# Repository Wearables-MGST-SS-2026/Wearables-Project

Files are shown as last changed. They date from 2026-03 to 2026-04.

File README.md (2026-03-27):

# Wearables-Project

## Systemarchitektur

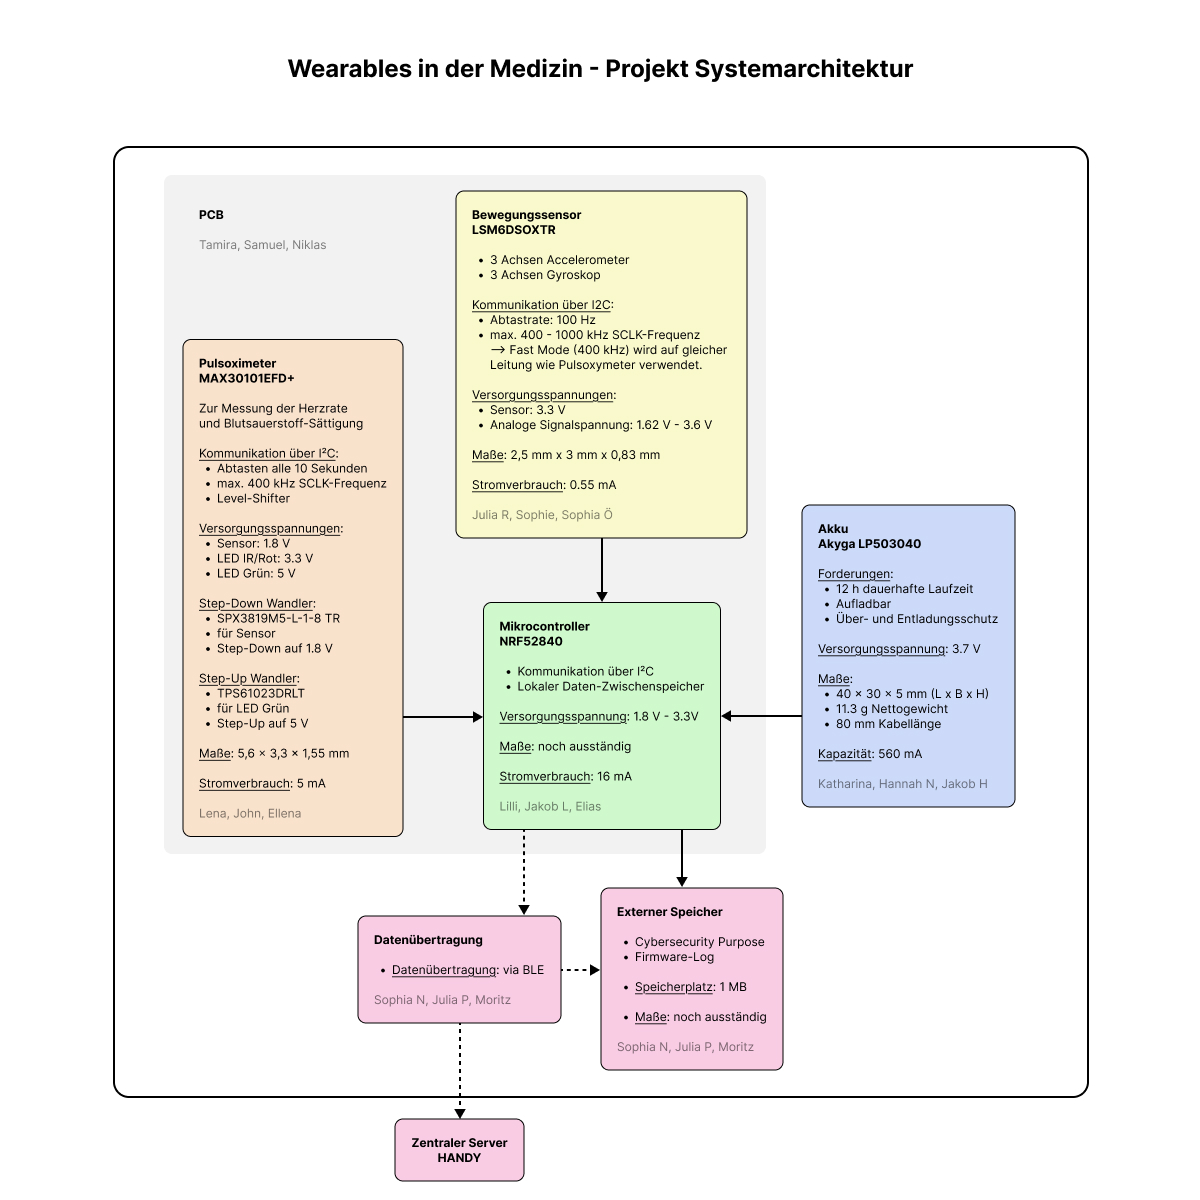
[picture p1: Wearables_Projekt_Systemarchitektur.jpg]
Systemarchitektur


Links für die Bauteile:
- Mikrokontroller: https://www.digikey.at/de/products/detail/nordic-semiconductor-asa/NRF52840-QIAA-F-R/15929794
- Akku: https://www.conrad.at/de/p/akyga-lp503040-akkupack-x-spezial-akku-lipo-3-7-v-560-mah-3385838.html
- Externer Speicher: noch ausständig
- IMU: https://www.digikey.de/de/products/detail/stmicroelectronics/LSM6DSOXTR/9841882
- Pulsoximeter:
  - Sensor: https://www.mouser.at/ProductDetail/Analog-Devices-Maxim-Integrated/MAX30101EFD%2BT?qs=sITqEBh490kEm6CNcTH1tQ%3D%3D&srsltid=AfmBOooeisLKsf-SlCmX0eI9FAGqsr9U439F-9ioyHP3WWO6gMZ4mlS4&utm_source=chatgpt.com
  - Step-Down Wandler: https://www.mouser.at/ProductDetail/MaxLinear/SPX3819M5-L-1-8-TR?qs=S%2FCBhQS5rCpfutlZ3lVq4g%3D%3D
  - Step-Up Wandler: https://www.mouser.at/ProductDetail/Texas-Instruments/TPS61023DRLT?qs=BJlw7L4Cy78Zr3IJIU3gNw%3D%3D
  - Level-Shifter für I2C: https://www.mouser.at/ProductDetail/Texas-Instruments/PCA9306DCTR?qs=wgAEGBTxy7mysSrdibj0NQ%3D%3D

### Bauteilanforderungen an Akku 
Strom_Spannungsanforderungen

## 🗓️ Deadlines

##### ➡️ 17.03.2026 (Intern)
Bauteilauswahl der verschiedenen Gruppen + eine Person, welche diese vorstellt

##### ➡️ 31.03.2026 (Extern)
Funktionalität, Architektur 
Abgabe eines Dokuments von Projektleitungsgruppe (nach Absprache mit Gesamgruppe) 

##### ➡️ 12.04.2026 (Intern)
Schaltpläne Fertigstellung

##### ➡️ 27.04.2026 (Intern)
PCB Fertigstellung

##### ➡️ 30.04.2026 (Extern)
Schaltplan und Dokumentation (Verifikation Konzept, Cybersicherheit Risiken und Konzept) 
Jede Gruppe gibt zwei Dokumente ab für ihr jeweiliges funktionales Modul:
- Schaltplan in KiCad + Bill of Materials (Teile müssen in Stock sein und JEDES Bauteil muss aufgeführt werden) 
- Dokument für Messverfahren für Verifikation und Herstellung, 2 Seiten max.)

Projektleitungsgruppe gibt ein zusätzliches Dokument bzgl. Cybersicherheit Risiken und Konzept ab 

##### ➡️ 26.05.2026 (Extern)
Wearable Challenge Tag (Alle Gruppen führen die Tests gleichzeitig)

## System Anforderungen
- am Handgelenk tragbares Wearable (Wearable zu definieren!) mit: 
  - 12 Stunden ununterbrochene Funktionalität
  - wiederaufladbare Akku (Ladebuchse muss nicht mit im Gehäuse eingeplant werden, Drahtloses laden nicht notwendig)
    - Spannungsregler notwendig? 
  - Datenübertragung zum zentrale Server
    - welche Übertragung wird genutzt? sowohl intern als auch extern= 
  - Pulsmessung
  - Bewegung Messung (min. 3 Achsen Accelerometer, min. 3 Achsen Gyroskop)
  - IPX7 Schutzklasse
  - kein User interface
  - kein Display
  - 1 Jahr Kundengarantie -> muss nach 1 Jahr immer noch 12 Stunden Laufzeit haben
  - IMU soll 100Hz Abtastrate haben
  - alle Daten müssen am Ende des Tages MIT timestamps auf dem Server sein (Sekundär Batterie muss NICHT implementiert werden), es kann angenommen werden dass Server ständig verbunden ist, aber es muss sicher gestellt werden dass keine Blockierungen passieren
  - Pulsoxy/ HR soll alle 10 Sekunden Herzrate messen & neuen Wert speichern

## Glossar
Wearable Definition:
Wearables bezeichnen Geräte, die folgende Kriterien erfüllen. Sie können nicht nur nicht obsturktiv am Körper getragen werden, sie schränken also keine Körperfunktionen ein, sondern können auch jederzeit durch die benutzende Person an- und abgelegt werden. Zudem bedienen sie sich der Sensorik, digitalen Datenverabreitung und der Kommunikation.

## Abgabe Anforderungen
- Schaltplan in KiCad designen
  - gewählte Bauteile müssen in KiCad einen Footprint besitzen
  - Testpunkte mitbedenken
  - Namen / Kennzeichnungen müssen mit Schaltplänen anderer Gruppen zusammenpassen 
- Bill of Materials:
  - Bauteile müssen kaufbar sein (keine Lieferzeiten von 12 Wochen o.ä.)
  - Eindeutige ID, Wert, Größe/Gehäuse und Bestellcode angeben
  - Beispiel BOM 
   

## Gruppen einteilung
#### Akku Gruppe 
Jakob, Hannah N., Katharina
#### Bewegungssensor Gruppe 
Julia R., Sophie, Sophia Ö. 
#### Pulsoxy/HR Gruppe 
Lena, John, Ellena
#### Projektleitunsgruppe 
Sophia G., Hauke, Marie, Hannah K. 
#### PCB Gruppe (unterstützt Akku Gruppe) 
Tamira, Niklas, Samuel 
#### Mikrokontroller Gruppe 
Jakob, Elias, Lilli 
#### Datenverarbeitungsgruppe 
Sophia N., Pietschie, Moritz

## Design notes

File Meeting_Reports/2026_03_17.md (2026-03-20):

### Update Anforderungen 
- 1 Jahr Kundengarantie -> muss nach 1 Jahr immer noch 12 Stunden Laufzeit haben 
##### IMU
- soll 100Hz Abtastrate haben

##### Datenübertragung 
- alle Daten müssen am Ende des Tages MIT timestamps auf dem Server sein (Sekundär Batterie muss NICHT implementiert werden)
- es kann angenommen werden dass Server ständig verbunden ist 
- es muss sicher gestellt werden dass keine Blockierungen passieren

##### Pulsoxy/ HR
- alle 10 Sekunden Herzrate messen & neuen Wert speichern 

### Bauteilauswahl 
#### Pulsoxy/HR
MAX30101 
- I2C
  - 400khZ maximale SCL clock freqeuncy 
- VLed grün braucht 5V
- VDD-1,8V
- ViR und Vred -> 3.3V
- 5mA

#### IMU
LSM6DS
- I2C 
  -  clock frequenzy 1000kHz (fast plus mode) 
  -  400kHZ (fast mode) -> geht auf gleicher Leitung wie HR/Pulsoxy sensor 
- 0.55 mA 
- 3,3V Versorgungsspannung 
- 1.62V-3.6V analoge Signalspannung 

#### Mikrokontroller 
nRF52840 
- BLE übertragung 
- 1,8-3,3V versorgungsspannung
- 16mA 

#### Akku 
Akyga LP503040
- 560mA 
- 3.7 V
- Kabellänge: 80 mm
- Länge: 40 mm
- Breite: 30 mm
- Höhe: 5 mm
- Nettogewicht: 11.3 g

### TO DO: 
- akku systemblock diageramm dings (Leitung) 
- systemarchitektur updaten mit ausgewählten Bauteilen (Sophia) 
- update read.me mit neuen Kundenanforderungen 

### Fragen 

### Sonstiges

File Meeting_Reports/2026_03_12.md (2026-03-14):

# Meeting Report - 12. März

Interne Deadlines:
* Bauteile raussuchen bis 17.03.
* Schaltpläne bis 12.04.
* PCB bis 27.04.

## General
* Systemarchitektur: EKG fällt weg, weil Puls bereits beim Pulsoxi gemessen wird
* Teams können intern eigene Projects mit Issues erstellen, aber sollten alles Wichtige im großen Project dokumentieren
* Aitor zum Repo einladen

## Gruppe Projektleitung
* Funktionalität basiert auf einer IU (Intended Use) + Kommunikation + Spannung

## PCB Gruppe
* Switch auf KiCad

## Gruppe Akku
* Überladungs- und Entladungsschutz einbauen (weil Medizinprodukt)
* KEIN Ladeszenario, nur Konzept (Wireless Charging oder so, muss aber eben nicht ins Design implementiert werden)
* Blockdiagramm erstellen (Tool: Webench Power Designer)

## Gruppe Datenübertragung
* Zentraler Server = Handy (muss nicht noch weiter übertragen werden)

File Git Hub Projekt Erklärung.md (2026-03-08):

### Repository
#### Dokumente 
Repository dient als Aufbewahrungsort für alle wichtigen Dokumente: 
- Erklärungsdokumente
- Dokumente für Abgaben (Schaltpläne, etc.)
- andere wichtige Dokumente (z.B. PCB Design Guidelines)

Alle sollten Berechtigung haben Dokumente zu bearbeiten und neue Dokumente hinzuzufügen.

#### Issues Übersicht
Im Repository selbst können ALLE assozierten Issues/To Dos eingesehen werden, die Verwaltung dieser ist jedoch einfacher über das Projekt selbst (siehe unten). 

### Project
Das Projekt 'Wearables Projekt Übersicht' ist mit dem Repository verbunden und wird für die gesamte Organisation des Gruppenprojekt genutzt. 
Es gibt verschiedene Ansichten um das Projekt und alle Issues zu sehen: 
- Backlog
- Board
- Calendar
- My items
  
#### Organisatorisches 
##### Meeting Protokolle & Agendas 
- Protokollierung aller Meetings wird von der Projektleitungsgruppe, damit alle auf dem gleichen Stand sind
- Erstellung von To Do's als Issues 
- Erstellung von Agendas für das jeweilige nächste Meeting von der Projektleitungsgruppe im vorhinein
  - Bearbeitbar von Allen falls weiter Punkte besprochen werden müssen

- Bei zusätzlichen kleineren Meetings mit anderen Gruppen, z.B. Akkugruppe mit Mikrokontrollergruppe, erstellt bitte ein Issue mit kurzen Notizen was besprochen wurde oder welche Entscheidungen getroffen wurde, dadurch bleiben auch in Krankheitsfällen o.ä. alle auf dem gleichen Stand. 

##### Labels & Target Dates
- Versehen aller Issues mit Labels und Target Dates -> zeitliche Dringlichkeit sichtbar in Kalender view & Filterung nach Labels für jeweilige Gruppen möglich <br>
  → Wenn ihr weitere Issues erstellt, benutzt bitte Labels und Target Dates! 

##### Assignees 
Diesen Punkt besrpechen wir im Meeting am 12.März 

##### To Do / In progress / Done 
Bitte verschiebt eure Issues in die jeweiligen Kategorien, damit es übersichtlich bleibt und alle sehen können auf welchem Stand wir gerade sind. 

#### Discussions 
Die Diskussions Funktion ist wie ein Forum und kann für alles benutzt werden, was nicht bis zum nächsten Meeting warten kann o.ä., dadurch bleibt alles etwas übersichtlicher und ist leicht wieder zu finden. Bitte erstellt relevante Categorys für euer Anliegen.

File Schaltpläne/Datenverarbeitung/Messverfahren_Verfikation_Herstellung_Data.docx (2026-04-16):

Messverfahren für Verifikation und Herstellung Datenübertragen

A. Bluetooth-Verbindung (Antenne)

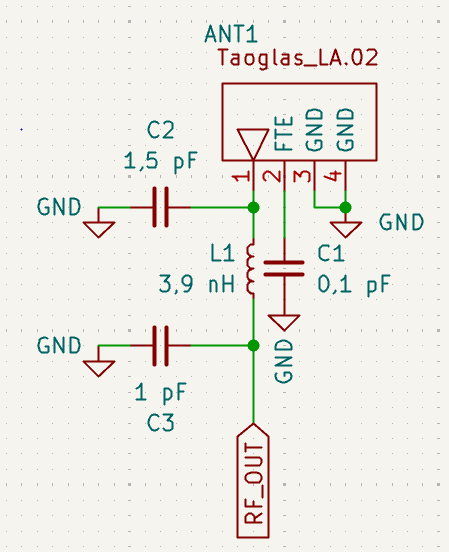
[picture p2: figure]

1. Verifikationstest (Entwicklung)

Test 1: Auffindbarkeit Testen

Überprüfen, ob das Wearable BLE-Advertising-Pakete sendet und vom Endgerät auffindbar ist.

Ablauf:

1. Wearable anschalten und in Pairing-Modus (Advertising aktivieren)
2. Scan-App/ BLE-Einstellung des Endgeräts zum Suchen nutzen
3. MAC-Adresse und Broadcast-Name prüfen
4. Wiederholen in 1m, 3m, 5m Entfernung

Erwartung:

- Wearable signalisiert Pairing-Bereitschaft
- Wearable ist auffindbar
- Name und Adresse stimmen mit Programmierung überein
- Entfernungen können toleriert werden

Test 2: Signalstabilität (RSSI/ Received Signal Strength Indicator)

Überprüfen, ob die RSSI unter Last stabil ist, um sicherzustellen, dass eine zuverlässige Verbindung gewährleistet werden kann (Antenna-Matching). Für diesen Test wird eine UART-Konsole/RSSI-Monitoring-App sowie Endgerät und Wearable benötigt.

Ablauf:

1. Wearable und Endgerät koppeln mit 1m Distanz
2. UART muss BLE_CONNECTED zeigen
3. 60s Referenzmessung
4. 60s Stresstest: Hand auf Wearable (Dämpfung durch Körper)
5. 5min Langzeittest

Erwartung:

- Referenzmessung: -40dBm bis –60dBm (bei 1m Distanz)
- Stresstest: RSSI-Abfall < 20dBm
- Langzeittest: keine Verbindungsabbrüche (BLE_DISCONNECTED)
- RSSI-Schwankung <5dBm
2. Herstellungstest

Für beide Tests wird zusätzlich zum Wearable und dem Endgerät ein UART benötigt.

Test 1: Verbindungsstatus und Fehler-Auswertung

Ablauf:

1. Wearable einschalten und über den Prüfadapter eine Verbindung zum Test-Endgerät erzwingen. Den UART-Stream auf das Event "Connected" scannen. Automatische Hardware-Diagnose beim Systemstart ausführen.
2. Ein Test-Datenpaket vom Endgerät an das Wearable senden und das Quittierungssignal (ACK) im UART-Log abfangen.
3. Die Verbindungsparameter während einer aktiven Sitzung aus dem Controller-Stack auslesen (via HCI-Kommandos).
4. Den Zeitraum zwischen Start des Advertisings und Timeout überwachen.

Level 1: Info

- Fokus: Verbindungsstatus
- Ausgabebeispiel: BLE_CONNECTED, BLE_DISCONNECTED
- Bedeutung / Ziel: Bestätigt, dass der Handshake erfolgreich war und das Wearable die Funkverbindung hält.

Level 2: Data

- Fokus: Paket-Überprüfung
- Ausgabebeispiel: Sent: [0xAF, 0x01, 0xFF], ACK received
- Bedeutung / Ziel: Prüft, ob die Datenrate für Firmware-Updates (OTA) und Sensordaten optimiert ist.

Level 3: RF/Stack

- Fokus: Protokoll-Ebene
- Ausgabebeispiel: HCI Event: Command Complete, Connection Interval: 30ms
- Bedeutung / Ziel: Verifiziert die Energieeffizienz und die korrekte Signalaushandlung der Antenne.

Level 4: Error

- Fokus: Fehlersuche
- Ausgabebeispiel: ERROR: Advertising Timeout
- Bedeutung / Ziel: Funktions-Check: Wearable hat niemanden zum Koppeln gefunden (Endgerät prüfen).

Level 4: Error

- Fokus: Fehlersuche
- Ausgabebeispiel: Crystal Oscillator unstable
- Bedeutung / Ziel: Hardware-Check: Der 32MHz Quarz ist schlecht verlötet oder defekt. Gehäuse muss getauscht werden.

Test 2: Re-Connectivity

Überprüfen, ob die Verbindung nach Trennung automatisch wieder aufgenommen wird.

Ablauf:

1. Verbindung herstellen

2. Verbindungsabbruch durch:
a) Endgerät außerhalb der Reichweite
b) Bluetooth deaktivieren
3. Geräte wieder annähern/ Bluetooth reaktivieren

Erwartung:

- Wearable startet automatisch das Advertising

B. Flash-Speicher (Cybersecurity)

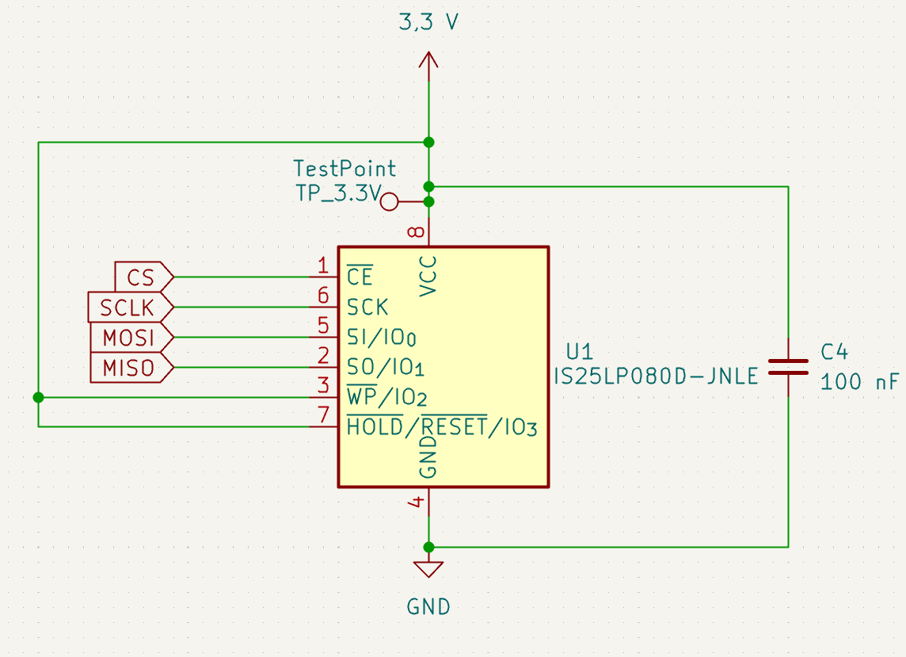
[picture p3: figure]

Testpunkt:

- TP_3.3V: Testen der Versorgungsspannung VCC
- TP_GND: Referenzmasse für Messungen

1. Verifikationstests
Test 1: Verifikation der Versorgungsspannung

Überprüfung, ob VCC = 3.3 V entspricht und unter Last stabil bleibt.

Ablauf:

1. Multimeter Sonden an TP_3.3V (rote Sonde) und TP_GND (schwarze Sonde) anlegen
2. Labornetzteil auf 3.3 V einstellen
3. DC-Spannung am Multimeter ablesen
4. Lastprüfung: Oszilloskop an TP_3.3V anschließen und AC-Kopplung zur Messung des Spannungsrippels aktivieren, während Speicher aktiv ist.

Erwartung:

- DC-Wert: 3,3 V ± 5%
- Spannungsripple unter Last: < 50mV (Peak-to-Peak)

Test 2: Verifikation der Speicherfähigkeit

Überprüfung, ob der Flash-Speicher korrekt auf Adressanfragen reagiert und gespeicherte Daten richtig zurückgibt. Der Test wird durch eine Firmware auf dem Mikrocontroller ausgeführt

Ablauf:

1. System starten und Flash-Speicher initialisieren
2. Chip Select aktivieren (auf LOW setzen)
3. Sektor löschen und bekannten Wert an definierte Adresse schreiben
4. Leseanfrage über SPI-Schnittstelle an Speicher senden
5. Adresse übertragen
6. Daten von Speicher empfangen und Chip Select deaktivieren (auf HIGH setzen)

Erwartung:

- Gelesene Daten entsprechen den zuvor geschriebenen Werten
- Bei wiederholter Abfrage derselben Adresse werden identische Datenwerte geliefert

2. Herstellungstests

Schritt | Prüfschritt | Testpunkt | Bewertungskriterium
1 | Spannungsprüfung | TP_3.3 V & TP_GND | 3.3 V ± 5%, stabil
2 | Schnittstellencheck | Über SPI | Gültige Hersteller-ID (0x9D)
3 | Write-Test | Über SPI | Schreiben ohne Fehler
4 | Read Test | Über SPI | Gelesene Daten = geschriebene Daten
5 | Endbewertung | | Bauteil als funktional oder fehlerhaft markieren

Für die Durchführung wird ein Prüfadapter mit Kontaktierung der relevanten Testpunkte sowie eine mikrocontrollerbasierte Teststeuerung (z. B. SPI-Testprogramm) benötigt.

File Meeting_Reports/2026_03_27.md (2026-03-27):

### Schaltpläne 
- Erinnerung Deadline 12.4 bis dann müssen Schaltpläne & Bill of Materials 
- Verbindungen mit Kontaktgruppen (v.a. Akku, Mikrokontroller) -> einigt euch wer welche welche Bauteile einplant die dazwischen sind 
- Testpunkte/ Kontaktpunkte für Programmierung 
- Erinnerung Messverfahren Dokument für Verifikation und Herstellung muss auch abgegeben werden (pro Gruppe) 

### 1. Abgabe - Funktionalität & Systemarchitektur 
- durchlesen bitte und KOmmentare an uns: 
https://github.com/Wearables-MGST-SS-2026/Wearables-Project/blob/main/Funktionalit%C3%A4t.md

### Sonstiges 
- bitte updated den Progress bei euren issues regelmäßig

### Fragen an Aitor 
- externer Speicher für Cybersecurity notwendig -> benutzt den kleines Flashspeicher mit 1Mb Speicher 
- Timestamps müssen im Konzept von der Mikrokontrollergruppe beachtet werden

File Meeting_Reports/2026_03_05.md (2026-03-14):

### Besprochene Punkte:
#### Entwicklung
Kunden Anforderungen inklusive Klärung noch offener Fragen, siehe aktuell definierte Anforderungen in readme.md
Systemarchitektur: gemeinsame Ausarbeitung, siehe aktuellen Stand in readme.md

#### Gruppeneinteilung
Siehe Gruppeneinteilung und Zuteilung in read me file, jede Gruppe ist für ein funktionales Modul verantwortlich mit zwei Besonderheiten:
- Die Gruppe, welche das finale PCB designt hat kein eigenes funktionales Modul, aber unterstützt die Akku Gruppe, da der Akku das aufwändigste Modul ist
- Die Projektleitungsgruppe hat ebenso kein eigenes funktionales Modul, aber es wird kontinuierlich besprochen welche andere Gruppe möglicherweise Unterstützung braucht
Entscheidung über zu benutzende Software für Schaltplan Erstellung: KiCud, wichtig hierbei ist, dass die verwendeten Bauteile in KiCad ein Design footprint haben

#### Fragenklärung
Fragenklärung bzgl. welche Aufgaben von wem ausgearbeitet & abgegeben werden müssen:
- Alle Dokumente welche als Gesamtgruppe abgegeben werden müssen ( Funktionalität & Architektur, Cybersicherheit Risiken & Konzept), werden von der Projektleitungsgruppe verfasst und abgegeben, nach gemeinsamer Besprechung und Beitragen aller
- Alle von Untergruppen abzugebende Dokumente (Schaltpläne für funktionales Modul, Messverfahren für Verifikation & Herstellung) werden von den jeweiligen Gruppen verfasst und nach Prüfung auf Kompatibilität mit anderen Gruppen abgegeben
- ALLE Untergruppen müssen nach vollständigem Design und Abgabe ein eigenes Gehäuse konstruieren und bauen für die Testung

#### Organisatorisches
Die Projektleitungsgruppe wird zeitnah eine Agenda für das nächste Meeting erstellen, mit allen zu besprechenden Punkten, bei Besprechungswünschen fügt euren Agendapunkt im vorhinein hinzu oder kontaktiert die Projektleitungsgruppe mit Wünschen & Anregungen
Nach den Meetings wird die Agenda mit dem Besprochenen ausgefüllt und als Meetingprotokoll gespeichert, sollten im Nachhinein noch Informationen fehlen, bitte als Kommentar zu fügen, damit
Alle wichtigen Informationen zum Projekt sind in der Readme File zu finden
Alle wichtigen Informationen bzgl. des Repositoriers (Erklärungen zur Nutzung etc.) sind in der git Hub Projekt Erklärung File zu finden.

#### To dos
- Recherche der einzelnen Gruppen bzgl Bauteilen/Möglichkeiten bis zum nächsten Meeting (12. März)
- Leitungsgruppe setzt Git-Repository auf, teilt es und erklärt in nächstem Meeting (12. März)
- Leitungsgruppe protokolliert dieses Meeting und setzt Agenda für nächstes auf

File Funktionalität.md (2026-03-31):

### Funktionalität
Das System ist ein am Handgelenk tragbares Wearable zur kontinuierlichen Erfassung von Vital- und Bewegungsdaten im Alltag. Es dient der Erhebung von Daten zur Herzfrequenz, Sauerstoffsättigung sowie Bewegungsinformationen des Nutzers.
Die erfassten Daten werden drahtlos an ein externes Endgerät, beispielsweise ein Smartphone, übertragen und dort gespeichert. Das Wearable selbst verfügt über keine Anzeige- oder Bedienelemente und arbeitet vollständig autonom im Hintergrund.
Das System ist für den täglichen Einsatz über eine typische Nutzungsdauer von 12 Stunden ausgelegt und für wiederholte Ladezyklen konzipiert.  Es ist für den Einsatz im Alltag geeignet und gegenüber äußeren Einflüssen wie Feuchtigkeit geschützt, sodass ein Betrieb auch bei Kontakt mit Wasser möglich ist.
Die Funktionalität basiert auf dem Zusammenspiel von Sensorik, zentraler Verarbeitungseinheit, Energieversorgung und drahtloser Kommunikation, wie in der Systemarchitektur dargestellt.
#### Grundlegender Ablauf
Das Wearable erfasst kontinuierlich Daten des Nutzers, verarbeitet diese intern und überträgt sie anschließend drahtlos an ein externes System. Eine zentrale Recheneinheit steuert dabei alle Abläufe innerhalb des Systems.
#### Datenerfassung
Die Erfassung der Nutzerdaten erfolgt über zwei zentrale Sensor Komponenten.
Ein Pulsoximeter erfasst Daten auf optischem Wege, sodass die Herzfrequenz sowie die Sauerstoffsättigung des Blutes berechnet werden können. Dazu wird Licht in die Haut eingestrahlt und die Reflexion des Lichts durch das Blut analysiert. Durch die periodischen Änderungen des Blutvolumens infolge des Herzschlags kann die Herzfrequenz bestimmt werden. Gleichzeitig ermöglicht die unterschiedliche Absorption von Licht die Abschätzung der Sauerstoffsättigung.
Die Messung erfolgt in regelmäßigen Intervallen und liefert diskrete Vitaldaten.
Zusätzlich erfasst eine Inertiale Messeinheit (IMU) kontinuierlich Bewegungsdaten. Diese misst lineare Beschleunigungen sowie Rotationsbewegungen in allen drei Raumachsen. Dadurch können sowohl Bewegungen als auch Lageänderungen des Handgelenks erfasst werden.
Die Sensoren sind direkt an die zentrale Verarbeitungseinheit angebunden und liefern ihre Messwerte fortlaufend an das System.
#### Datenverarbeitung
Die Verarbeitung der Sensordaten erfolgt durch den Mikrocontroller, der als zentrale Steuereinheit des Systems fungiert.
Er übernimmt das Auslesen der Sensordaten, deren zeitliche Zuordnung sowie die strukturierte Aufbereitung. Alle Daten werden mit Zeitstempel versehen, um eine spätere Auswertung zu ermöglichen.
Das System ist so ausgelegt, dass die Datenverarbeitung kontinuierlich erfolgt und keine Unterbrechungen im Datenfluss entstehen. Bei Bedarf werden Daten temporär gespeichert.
#### Datenübertragung
Die aufbereiteten Daten werden drahtlos über eine integrierte Kommunikationseinheit an ein externes Endgerät, beispielsweise ein Smartphone, übertragen.
Daten werden im Mikrokontroller temporär zwischengespeichert und für die Übertragung zum Server verarbeitet. Es wird sichergestellt, dass alle erfassten Daten vollständig und ohne Verlust und mit Timestamps übertragen werden. Bei temporären Verbindungsunterbrechungen erfolgt eine Zwischenspeicherung im System.
#### Energieversorgung
Die Energieversorgung des Systems erfolgt über einen wiederaufladbaren Akku. Dieser ermöglicht einen kontinuierlichen Betrieb über einen typischen Nutzungstag von 12 Stunden. Die Aufladung erfolgt über einen kabelgebundenen Anschluss mit integrierter Spannungsanpassung sowie Schutzmechanismen gegen Überladung.
Zur Sicherstellung eines stabilen Betriebs werden die einzelnen Komponenten mit den jeweils benötigten Spannungen versorgt. Die Energieverteilung ist so ausgelegt, dass ein effizienter und zuverlässiger Betrieb gewährleistet ist. Zusätzlich sind Schutzmechanismen gegen Über- und Tiefentladung integriert, um die Lebensdauer des Akkus zu erhöhen und die Betriebssicherheit zu gewährleisten.

### Glossar 
#### Wearable: 
nicht obstruktives Tragen am Körper getragen werden ohne Einschränkung von Körperfunktionen
An- und ablegbar durch die benutzende Person
Integrieren und Kombinieren Sensorik, Datenverarbeitung und Kommunikation

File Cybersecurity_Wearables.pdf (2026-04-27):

Medizin-, Gesundheits- und Sporttechnologie | MCI Innsbruck | 2026

# Cybersicherheitskonzept - Wearable Projekt

### 1. Identifikation der schützenswerten Daten

Das Wearable erfasst folgende Daten, die unterschiedlich schützenswert eingestuft werden:

Datentyp | Beschreibung / Schutzbedarf
Pulsdaten (PPG) | Herzfrequenz via MAX30101 – anonym erfasst, kein Personenbezug, geringer Schutzbedarf
SpO2-Daten | Sauerstoffsättigung – anonym erfasst, kein Personenbezug, geringer Schutzbedarf
IMU-Daten | Bewegungs-/Lagedaten – anonym erfasst, kein Personenbezug, geringer Schutzbedarf
Akkustand (AKKU_LEVEL) | Gerätestatus – geringer Schutzbedarf
Firmware-Image | Intellectual Property, Manipulationsschutz kritisch

Es handelt sich um ein Medizinprodukt im Sinne der EU-MDR. Die Daten werden anonym und ohne direkten Personenbezug erfasst, weshalb diese nicht weiter geschützt werden müssen. Eine ärztliche Auswertung ist nicht vorgesehen. Die Sicherheitsanforderungen der MDR sind dennoch einzuhalten, insbesondere hinsichtlich Integrität und Verfügbarkeit der Messdaten sowie des Schutzes der Firmware.

### 2. Bedrohungsanalyse (STRIDE)

Basierend auf dem STRIDE-Modell wurden folgende relevante Bedrohungen identifiziert:

Bedrohung | Szenario | Angriffsvektor
Spoofing | Fremdes Gerät gibt sich als Wearable aus | Bluetooth (BLE)
Tampering | Manipulation der Firmware über SWD-Pins | Physischer Zugriff auf PCB
Information Disclosure | Mitlesen von Gesundheitsdaten per BLE-Sniffer | BLE (Man-in-the-Middle)
Information Disclosure | Firmware-Extraktion über SWD-Schnittstelle | Physischer Zugriff auf PCB

Medizin-, Gesundheits- und Sporttechnologie | MCI Innsbruck | 2026

### 3. Schutzmaßnahmen

### 3.1 Authentifizierung der BLE-Verbindung

- Da die übertragenen Messdaten keinen Personenbezug aufweisen, ist eine Datenverschlüsselung nicht erforderlich. Der Fokus liegt auf der Authentifizierung, so dass ausschließlich autorisierte Geräte eine Verbindung aufbauen können.
- BLE-Kommunikation ausschließlich mit zuvor gekoppelten und gebondeten Endgeräten (Kopplung nur im initialen Setup oder im definierten Service-Modus).
- Einsatz einer Device-Whitelist (Filter Accept List): Nur bekannte, registrierte Smartphones dürfen eine Verbindung aufbauen.
- BLE-Pairing mit Bonding über LE Secure Connections (LESC) mit Elliptic Curve Diffie-Hellman (ECDH) stellt sicher, dass nur authentifizierte Geräte kommunizieren können.
- Re-Pairing nur nach kontrolliertem Reset oder expliziter Freigabe durch den Nutzer – verhindert unbefugtes Einbinden fremder Geräte.

### 3.2 Datenschutz auf dem Gerät (lokaler Speicher)

Messdaten werden nur im Notfall temporär lokal auf dem nRF52840-Flash gespeichert. Da kein Personenbezug besteht, ist keine Verschlüsselung erforderlich. Nach erfolgreicher Übertragung an das Smartphone werden die lokalen Daten gelöscht.

### 3.3 Sichere Firmware-Updates (OTA via BLE)

Firmware-Updates werden im Feld ausschließlich über Bluetooth Low Energy per Nordic Secure DFU des nRF52840-SDK eingespielt:

- Es ist dauerhaft Platz für mindestens zwei Firmware-Images reserviert (Dual-Slot-Prinzip) – die neue Firmware wird zunächst in einen separaten Slot geschrieben und erst nach erfolgreicher Validierung übernommen.
- Jedes Image wird vor dem Upload mit einer ECDSA-Signatur versehen und zweistufig geprüft: zuerst durch die laufende Firmware, dann erneut durch den Bootloader (Secure Boot) – unsignierte Images werden abgelehnt.
- Rollback-Schutz: Downgrades auf ältere Firmware-Versionen werden durch eine Versionsnummernprüfung im Bootloader verhindert.
- Speicherschutz: Der Bootloader ist lese- und schreibgeschützt, die aktive Firmware lesegeschützt und alle Firmware-Slots sind nach außen schreibgeschützt.
- Alle Änderungen und Änderungsversuche werden mit Zeitstempel in einem gesicherten Log erfasst.
- SWD-Schnittstelle: Wird ausschließlich bei der Erstprogrammierung in der Fertigung genutzt und ist im Betrieb über das APPROTECT-Register dauerhaft gesperrt.

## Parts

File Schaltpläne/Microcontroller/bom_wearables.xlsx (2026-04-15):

Bill of Materials Microcontroller
Supplier | Description | Part number | Dimensions (BxHxL) | Quantity | Cost | Availability | Link
Mouser | HF-System auf einem Chip - SoC Bluetooth 5, IEEE 802.15.4-2006, 2.4 GHz transceiver | NRF52840-QFAA-F-R |  | 1 | 7.22 € | from 28.08.2026 | https://www.mouser.at/ProductDetail/Nordic-Semiconductor/NRF52840-QFAA-F-R?qs=A6eO%252BMLsxmSdeoxcrQ6IBg%3D%3D
RS | RS PRO 32.768 kHz Quarz, ±10 ppm, 12.5 pF, B. 1.5mm, H. 0.8 mm, L. 3.2 mm, SMD, 2-Pin | 144-2326 (RS-Best. Nr.) | 1.5mm, 0.8mm, 3.2mm | 1 | 0.82 € | available | https://at.rs-online.com/web/p/schwingquarz/1442326
 | Kondensator 18pF |  |  | 2
 | Kondensator 1uF |  |  | 1
 | Kondensator 100pF |  |  | 1
 | Kondensator 100nF |  |  | 1
 | Kondensator 4.7uF |  |  | 1
 | Kondensator 4.8 nF |  |  | 1
 | Kondensator 12pF |  |  | 2
 | Widerstand 4.7kOhm |  |  | 2

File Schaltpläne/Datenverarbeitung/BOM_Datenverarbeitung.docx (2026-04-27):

Designator | Bauteil | Anzahl | Wert | Link
U501 | IS25LP080D-JNLE | 1 | | Flash-Speicher (https://www.mouser.at/ProductDetail/ISSI/IS25LP080D-JNLE?qs=pif5%252B9MYt0VFG57xzMjs6Q%3D%3D)
ANT501 | LA.02 TAOGLAS | 1 | | Antenne (https://www.mouser.de/ProductDetail/Taoglas/LA.02?qs=GmNq1OH0n5TZOlk%2FlWkapQ%3D%3D)
C501 | GJM1555C1H1R0WB01D | 1 | 1pF | Kondensator-1pF (https://www.mouser.de/ProductDetail/Murata-Electronics/GJM1555C1H1R0WB01D?qs=YLLXL5qGyDtaruZHJwTPNg%3D%3D)
C502 | GJM1555C1HR10WB01D | 1 | 0.1pF | Kondensator-0.1pF (https://www.mouser.de/ProductDetail/Murata-Electronics/GJM1555C1HR10WB01D?qs=tpjTAP4gRjgPNeW3TqnU9A%3D%3D)
C503 | GJM1555C1H1R5WB01D | 1 | 1.5pF | Kondensator-1.5pF (https://www.mouser.de/ProductDetail/Murata-Electronics/GJM1555C1H1R5WB01D?qs=YLLXL5qGyDucsRPozQcunA%3D%3D)
C504 | GRM155R71C104KA88J | 1 | 100nF | Kondensator-100nF (https://www.mouser.de/ProductDetail/Murata-Electronics/GRM155R71C104KA88J?qs=tpjTAP4gRjhjnwp0cMzUDQ%3D%3D)
L501 | LQG15HN3N9S02D | 1 | 3.9nH | Spule-3.9nH (https://eu.mouser.com/ProductDetail/Murata-Electronics/LQG15HN3N9S02D?qs=wJtOAfHdpWBH9pu3vTmamg%3D%3D)

Bill of Materials – Datenverarbeitung

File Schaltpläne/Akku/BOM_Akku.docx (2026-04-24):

Bill of material – Akku

Designator | Bauteil | Anzahl | Wert
BT201 | Akyga LP503040 Akkupack x Spezial-Akku LiPo 3.7 V 560 mAh Link BT201 (https://www.conrad.at/de/p/akyga-lp503040-akkupack-x-spezial-akku-lipo-3-7-v-560-mah-3385838.html) | 1
U201 | LTC3558EUD-TRPBF Link U201 (https://ttps://www.digikey.de/de/products/detail/analog-devices-inc/LTC3558EUD-TRPBF/1931655) | 1
R201 | RC0402FR-07100KL Link R201 (https://www.digikey.de/de/products/detail/yageo/RC0402FR-07100KL/726526) | 1 | 100k
R202 | ERA-8AEB224V Link R202 (https://www.digikey.de/de/products/detail/panasonic-industry/ERA-8AEB224V/3070888) | 1 | 220k
R203 | CR0402-FX-3243GLF Link R203 (https://www.digikey.de/de/products/detail/bourns-inc/CR0402-FX-3243GLF/3783314) | 1 | 324k
R204 | RC0402FR-07121KL Link R204 (https://www.digikey.de/de/products/detail/yageo/RC0402FR-07121KL/726536) | 1 | 121k
R205 | RN73R2ATTD2501B25 Link R205 (https://www.mouser.at/ProductDetail/KOA-Speer/RN73R2ATTD2501B25) | 1 | 2,5k
R206 | RT73F2A105KBTD Link R206 (https://www.digikey.de/de/products/detail/te-connectivity-passive-product/RT73F2A105KBTD/26269901) | 1 | 105k
R207 | MCA1206MF1502BP100 Link R207 (https://www.mouser.at/ProductDetail/Vishay-Beyschlag/MCA1206MF1502BP100?qs=Rp5uXu7WBW9Bl4UUrBYi8Q%3D%3D) | 1 | 15k
C201 | C0402C105K9PACTU Link C201 (https://www.digikey.at/de/products/detail/kemet/C0402C105K9PACTU/1090778) | 1 | 1µF
C202 | CL21A106KOQNNNE Link C202 (https://www.digikey.at/de/products/detail/samsung-electro-mechanics/CL21A106KOQNNNE/3886754) | 1 | 10µF
C203 | CL05C330JB5NNNC Link C203 (https://www.digikey.at/de/products/detail/samsung-electro-mechanics/CL05C330JB5NNNC/3886930) | 1 | 33pF
C204 | GRM188R60G226MEA0D Link C204 (https://www.digikey.at/de/products/detail/murata-electronics/GRM188R60G226MEA0D/2334877) | 1 | 22µF
C205 | C4532C0G3F331K250KA Link C205 (https://www.digikey.at/de/products/detail/tdk/C4532C0G3F331K250KA/789776) | 1 | 330pF
C206 | GRM0335C1E100JA01D Link C206 (https://www.digikey.at/de/products/detail/murata-electronics/GRM0335C1E100JA01D/4358173) | 1 | 10pF
L201 | MBKK2012T2R2M Link L201 (https://www.digikey.at/de/products/detail/taiyo-yuden/MBKK2012T2R2M/5035137) | 1 | 2,2µH

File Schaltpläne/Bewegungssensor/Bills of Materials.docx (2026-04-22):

Bill of Materials – LSM6DSOX

Designator | Comment | Quantity | Value
IMU300 | LSM6DSOXTR | 1 | LSM6DSOX
C301, C302 | GRM188R72A104KA35D | 2 | 100 nF

Links:

IMU: https://www.digikey.de/de/products/detail/stmicroelectronics/LSM6DSOXTR/9841882

Kondensator: https://www.digikey.at/en/products/detail/murata-electronics/GRM188R72A104KA35D/702549?srsltid=AfmBOopkq6qSfytrFK43KJe3v_0mkrz8BXgjI9Bxi2YC4qJfZeKDfNqQ

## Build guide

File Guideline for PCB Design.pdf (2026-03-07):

## PCB Design and Management Guideline

Design Rules

- Define stack-up (dielectric thickness, copper weight, impedance control) and design rules (clearances, trace/space, via sizes, annular ring, solder mask, paste) according to the Aisler PCB manufacturer before routing.
- When another PCB manufacturer is preferred, it shall be communicated before the start of the project.
- Avoid BGA footprints.
- Minimum size for passive components shall be 0402.
- Add Pin 1 marker to the Silkscreen if not already part of the footprint.
- Add polarity marker for Diodes to the Silkscreen if not already part of the footprint.
- Add name and version of the PCB to the Silkscreen.
- Add component unique IDs to the Silkscreen (close to each Part, in order to ease the soldering process). Exempted only if size does not allow it.
- Add connector IDS to the Silkscreen. If there is space, add the function of each connector to the silkscreen (i.e. Battery, IMU, Motor).
- Add polarity indicators (+, -) for Power connectors to the Silkscreen.
- Deviations from the given rules shall be communicated.

Project Naming:

- Altium projects shall be named with a name that includes some hint of the application and research project to which they belong.
- Project names shall have a maximum of 15 characters.
- Project names shall follow a camel case convention.
- Example: standSensorHub (Project = stand, Application = SensorHub)

Schematics:

- The components shall have an ordering code added to them to ease the ordering process. Check the availability before choosing a specific component.
- Generic components for passive elements shall not be used, always specify the value, footprint and ordering code. Tip: Use “Manufacturer Part Search” in Altium
- Perform a validation of the project and review all errors and warnings. Resolve the applicable ones.

PCB Design:

- Perform a “design rule check” and review all errors and warnings and resolve the applicable ones.
- Minimum coper to edge clearance shall be 10 mil (0,254 mm).
- Tip: As final step before review “remove dead copper” when pouring coper planes. (Shortcut: T-> G ->A)

Project Outputs:

- A Bill Of Materials (BOM) shall always be created.
- The components in the BOM shall be grouped by Value and ID to ease the soldering process.
- For Aisler, ODB++ format shall be chosen as assembly format (no Geber).

Component Orders:

- Provide a link to a shopping cart including all the components or provide an export of the shopping cart. The idea is that the person ordering the components imports the file into the corresponding supplier. Not following this rule will result in no order being placed.
- The person ordering the components is not responsible to check the availability of the single components.

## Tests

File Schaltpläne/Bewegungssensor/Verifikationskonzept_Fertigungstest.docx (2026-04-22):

Messverfahren für Verifikation und Herstellung

Wir haben spezifische Testpunkte (TP) in den Schaltplan eingebaut, um die kritischen Funktionen unseres Bewegungssensor-Moduls systematisch zu testen. Die Testpunkte ermöglichen einfache, reproduzierbare Messungen ohne beschädigte Lötstellen oder Platinen.

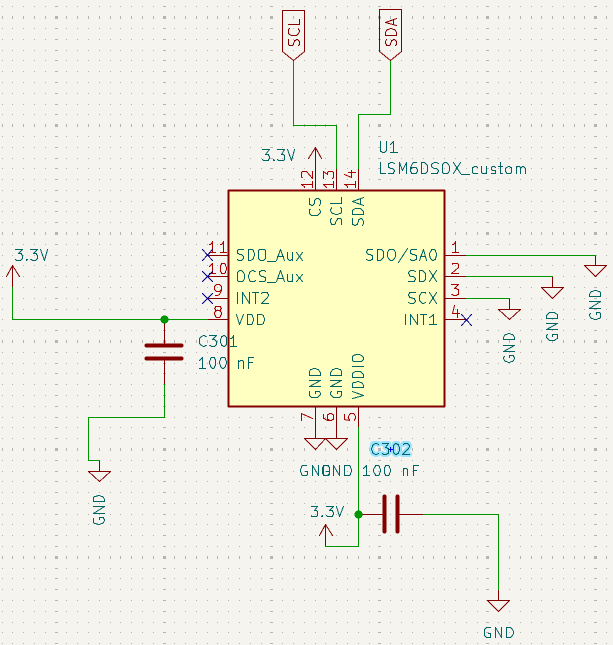
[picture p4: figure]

Testpunkte und ihr Zweck:

- TP101_VCC Versorgungsspannung VDD/VDDIO kontrollieren
- TP105_I²C_Block: I²C-Bus-Signale direkt am Mikrocontroller messen
- TP102_GND: als Referenzpunkt für alle Messungen.

Hinweis: Die Testpunkte TP1 TestPoint_VCC, TP_I²C_Block und TP2 TestPoint_GND sind im gemeinsamen nRF52840-Schaltplan der Mikrocontroller-Gruppe bereits vorhanden und werden deshalb in unserem Teilschaltplan nicht erneut eingezeichnet.

1. Verifikationstests (Entwicklung)

Test 1: Versorgung prüfen

Was testen? Die Versorgung VDD = 3.3 V des LSM6DSOX funktioniert zuverlässig
Wie?

1. Multimeter rote Sonde an TP_3.3V, schwarze an TP_GND
2. Labornetzteil vor dem DC/DC Wandler anschließen und den Sensor mit der vorgesehenen Systemversorgung betreiben (3.3V nominal)
3. Zusätzlich Grenzwerte 3.0 V und 4.2 V (Akku-Bereich) prüfen
4. Multimeter wieder abschließen bevor man Oszilloskop anschließt
5. DC-Spannung messen
6. Mit Oszilloskop direkt an der Versorgung den Ripple messen, dabei den Masseanschluss möglichst kurz halten

Erwartung:

- 3.25–3.35 V Versorgung
- Weiterhin funktionsfähige Versorgung zw. 3.0 V und 4.2 V
- Kleiner Ripple < 50 mV

→ TP_3.3V kontrolliert korrekte Sensor-Versorgung

Test 2: I²C-Kommunikation

Was testen? Sensor kommuniziert korrekt mit dem Mikrocontroller
Wie?

1. Arduino mit I²C-Scanner-Sketch anschließen
2. Oszilloskop an TP_SDA_μC und TP_SCL_μC anschließen
3. Schritt 1: Sketch starten → Serial Monitor auf Arduino prüfen
4. Schritt 2: Who_Am_I-Register (0x0F) des Sensors über I²C auslesen

Erwartung:

- Der Sensor antwortet auf einer der beiden möglichen I²C-Adressen: 0x6A (SA0-Pin low) oder 0x6B (SA0-Pin high)
- Beim Lesen des WhoAmI-Registers muss der Wert 0x6C zurückkommen
  - 0x6C = PASS
  - Jeder andere Wert = FAIL

→ TP_SDA_μC/TP_SCL_μC zeigen Bus-Signale

Test 3: Sensordaten auslesen

Was testen? Beschleunigung/Gyroskop des Sensors sind plausibel und werden korrekt über I²C gelesen
Wie?

1. Test-Sketch auf Arduino starten und Register für Beschleunigung und Gyroskop auslesen
2. Für den Beschleunigungssensor die Daten aus den Registern 0x28-0x2D lesen
3. Für das Gyroskop die Daten aus den Registern 0x22-0x27 lesen
4. Sensor 10 Sekunden ruhend loggen
5. Sensor mit einer Rotary Stage oder manuellen, definierten Drehung in mehreren bekannten/definierten Positionen bewegen und messen
6. Bei Arduino im Serial Monitor Werte auslesen und mit erwarteten Bereichen vergleichen

Erwartung:

- In Ruhezustand Beschleunigung ~1 g auf Z-Achse und ~0 g auf X und Y
- Bei Rotation ändern sich Gyrowerte entsprechend Bewegung
- Gewählte Messbereich von Gyroskop muss zur Testbewegung passen - ±250 dps (FS=±250) oder ±2000 dps (FS=±2000)
- Werte dürfen nicht unerwartet springen oder ausfallen

→ Bestätigt: Sensor liefert plausible Messdaten über I²C

2. Herstellungstests (Produktion)

Automatisierbarer Inline-Test (90 Sekunden/PCB):

Schritt | Messung | Testpunkt | Kriterium | Zeit
1 | Power-On | TP_3.3V/GND | 3.3 V ±5% | 10 s
2 | I²C-Scan | TP_SDA_μC/TP_SCL_μC | ACK 0x6A/0x6B | 20 s
3 | WhoAmI | Via I²C | Register 0x0F = 0x6C = PASS Register ≠ 0x6C = FAIL | 10 s
4 | IMU Self-Test | Via I²C | X/Y/Z ~ ±0.05 g (ruhend) FS = ±250 dps: 20-80 FS = ±2000 dps: 150-700 | 30 s
5 | Kennzeichnung des Prüfergebnisses (Sticker) | - | PASS oder FAIL | 20 s

Ausrüstung: Testfixture mit Federkontakten auf den TPs, Arduino-Skript, Labornetzteil und ggf. ein Multimeter für die Spannungsprüfung

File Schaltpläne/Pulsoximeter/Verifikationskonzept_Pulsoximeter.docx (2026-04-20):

Messverfahren für Verifikation und Herstellung

Wir haben spezifische Testpunkte (TP) in den Schaltplan eingebaut, um die kritischen Funktionen unseres Pulsoximeter-Sensors systematisch zu testen. Die Testpunkte ermöglichen einfache, reproduzierbare Messungen ohne beschädigte Lötstellen oder Platinen.

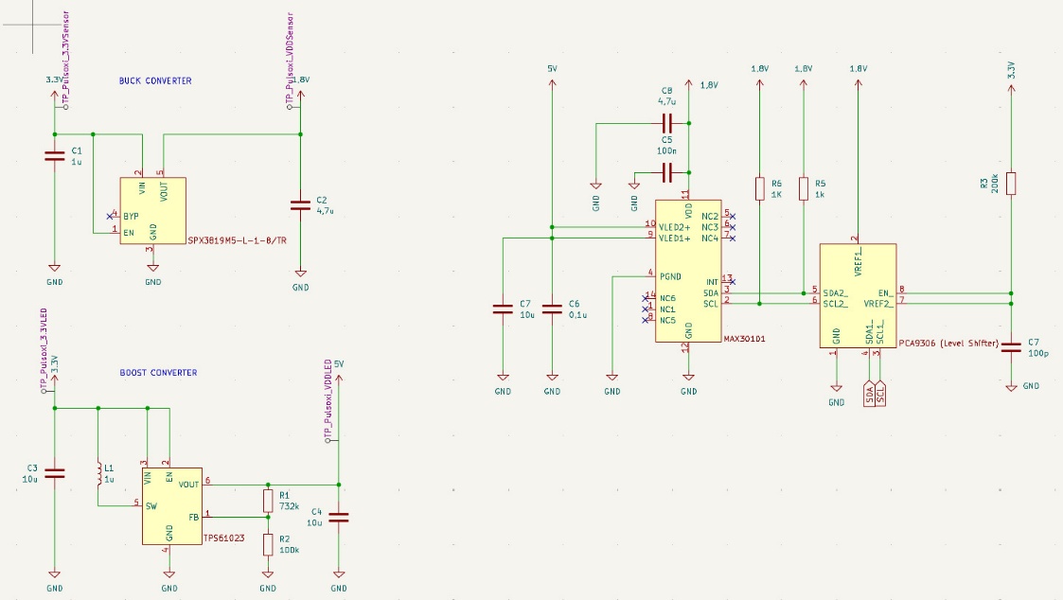
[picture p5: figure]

1. Verifikationstest (Entwicklung)

Buck Converter (SPX3819M5-L-1-8/TR)

Test 1: Ausgangsspannung prüfen

Was testen? VOUT = 1.8V

Wie? 1. Multimeter rote Sonde an TP_Pulsoxi_VDDSensor, schwarz an TP_GND

2. Lab-Netzteil 3.3V an TP_Pulsoxi_3.3VSensor anschließen

3. DC-Spannung messen + Ripple mit Oszilloskop

Erwartung: 1.71-1.89V, Ripple <20mV

- TP3 kontrolliert korrekte Buck Converter Ausgabe und somit auch die Versorgungsspannung des Pulsoximeters

Boost Converter (TPS61023)

Test 1: Ausgangsspannung prüfen

Was testen? VOUT = 5V

Wie? 1. Multimeter rote Sonde an TP_Pulsoxi_VDDLed, schwarz an TP_GND

2. Lab-Netzteil 3.3V an TP_Pulsoxi_3.3VLed anschließen

3. DC-Spannung messen + Ripple mit Oszilloskop

Erwartung: 4.75-5.25V, Ripple <50mV

- TP5 kontrolliert korrekte Boot Converter Ausgabe und somit auch die LED-Versorgungsspannungen

Pulsoximeter (MAX30101)

Test 1: Versorgungsspannung prüfen

- Siehe Buck Converter Test 1

Test 2: LED-Versorgungsspannung

- Siehe Boost Converter Test 1

Test 3: I²C-Kommunikation

Was testen? Sensor antwortet auf Mikrocontroller

Wie? 1. Arduino mit I²C-Scanner-Sketch anschließen

2. Oszilloskop an TP_SDA und TP_SCL anschließen

3. Sketch starten → Serial Monitor prüfen

Erwartung: Adresse 0xAE/0xAF gefunden, SCL 100-400kHz

- TP_SDA und TP_SCL zeigen saubere Bus-Signale

Test 4: Sensordaten auslesen

Was testen? Herzfrequenz und SpO2-Werte plausibel

Wie? 1. Finger auf die LEDs legen und Messung starten

2. gleichzeitig Referenzmessung an einem Referenzsensor starten

3. Ausgegebenen Werte des Sensors und des Referenzsensor vergleichen

Erwartung: Werte sollten bis auf eine kleine Abweichung gleich sein

- Bestätigung: Sensor liefert richtige Daten
2. Herstellungstests (Produktion)

Automatisierbarer Inline-Test (80 Sekunden / PCB):

Schritt | Messung | Testpunkt | Kriterium | Zeit
1 | Ausgangsspannung Buck Converter / Sensorversorgung | TP_GND / TP_Pulsoxi_VDDSensor | 1.8V ±2%, Ripple <20mV | 10s
2 | Ausgangsspannung Boost Converter / LED-Versorgung | TP_GND / TP_Pulsoxi_VDDLed | 5.0V ±5%, Ripple <50mV | 10s
3 | I²C-Scan | TP_SDA / TP_SCL | ADDR 0xAE/0xAF, SCL 100-400kHz | 20s
4 | WhoAmI | Via I²C | Register 0xFF = 0x15 | 10s
5 | Sensordaten | Via I²C | Plausible HR- & SpO2-Werte bei Fingerkontakt / Referenzwerte | 30s

Ausrüstung: Testfixture mit Federkontakten auf TPs + Arduino-Script

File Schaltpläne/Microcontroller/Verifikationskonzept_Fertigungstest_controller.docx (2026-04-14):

# Verifikations- und Testkonzept

# 1. Einleitung und Messverfahren

Dieses Dokument beschreibt die systematische Prüfung des nRF52840-Moduls. Wir nutzen die im Schaltplan implementierten Testpunkte (TP), um die Integrität der Spannungsversorgung, der digitalen Kommunikationsbusse (I²C/SPI) sowie der Programmierschnittstelle zu verifizieren. Ziel ist eine zerstörungsfreie Prüfung, die sowohl in der Entwicklungsphase als auch in der Serienfertigung reproduzierbare Ergebnisse liefert.

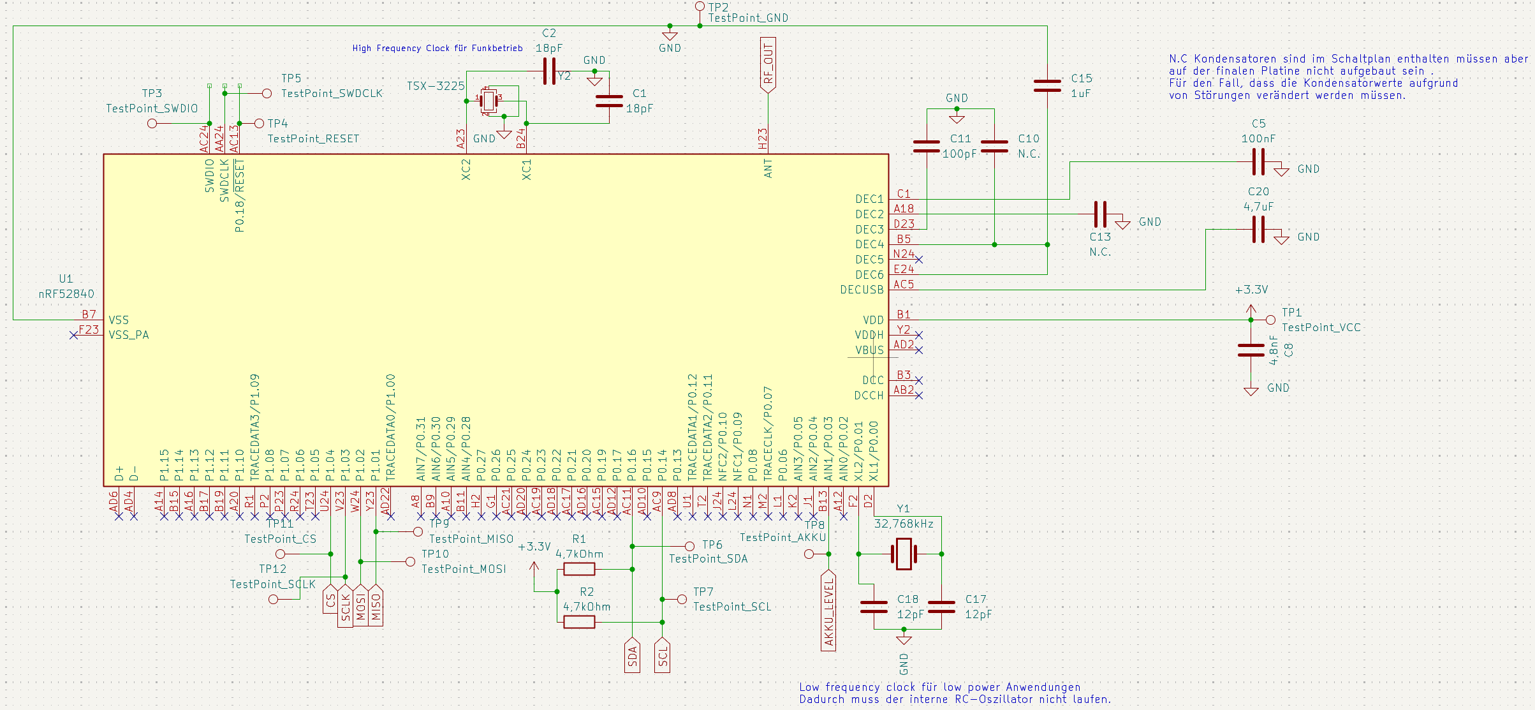
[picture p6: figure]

# 2. Detaillierte Testpunkt-Übersicht

Testpunkt | Zugehöriges Netz | Zweck der Messung
TP_VCC | +3.3V | Hauptversorgung des nRF52840 und der Peripherie.
TP_GND | GND | Bezugspotenzial für alle Messungen.
TP_SWD_Block | SWDIO / SWDCLK | Flashen der Firmware und Echtzeit-Debugging.
TP_RESET | P0.18 / nRESET | Hardware-Reset zur Initialisierung des Bootloaders.
TP_I2C_Block | SDA / SCL | Kommunikation mit I²C-Sensoren (z.B. LSM6DSOX).
TP_SPI_Block | MOSI/MISO/SCLK/CS | High-Speed Datentransfer zu externem Flash oder Displays.
TP_AKKU | AIN2 (P0.05) | Analogwertprüfung der Batteriespannung (Spannungsteiler).

# 3. Verifikationstests (Entwicklung)

Test 1: Power-Integrität und Decoupling

- Was testen? Stabilität der 3.3 V Schiene und Funktion der Filterkondensatoren.
- Wie? 3.3 V am Lab-Netzteil einspeisen. Messung mit Oszilloskop an TP_VCC gegen TP_GND.
- Erwartung: Spannung im Bereich 3.25 V – 3.35 V. Das Rauschen (Ripple) muss unter 50 mV liegen, um Funkstörungen zu vermeiden.

Test 2: Debugger-Connect & Grundfunktion

- Was testen? Ist der Chip via SWD erreichbar? Funktioniert der externe 32.768 kHz Quarz?
- Wie? Programmer (z.B. J-Link) an die SWD-Testpunkte anschließen. Auslesen der Device-ID via nRF Connect Desktop.
- Erwartung: Chip wird erkannt. Der externe Low-Frequency Clock (LFXO) wird in der Software erfolgreich gestartet (spart Strom im Sleep-Mode).

Test 3: I²C-Kommunikation

- Was testen? Sensor-Antwort und Signalqualität.
- Wie? Oszilloskop/Logic Analyzer an TP_SDA und TP_SCL.
- Erwartung: Korrekte I²C-Adresse (z. B. 0x6A) wird im Scanner erkannt. Saubere Pegel von 0 V bis 3.3 V ohne übermäßiges Überschwingen.

Test 4: SPI-Bus Validierung (Erweitert)

- Was testen? Integrität der High-Speed Datenübertragung zum externen Flash/Peripherie.
- Wie? 4-Kanal-Oszilloskop an TP_CS, TP_SCLK, TP_MOSI und TP_MISO. Eine Test-Sequenz (z. B. "WhoAmI" Register des SPI-Teilnehmers lesen) starten.
- Erwartung:
  - CS (Chip Select): Muss sauber auf LOW ziehen, solange die Kommunikation läuft.
  - SCLK (Clock): Taktfrequenz entspricht der Software-Einstellung (z. B. 8 MHz). Keine "verwaschenen" Flanken.
  - MOSI/MISO: Die Datenpakete müssen deckungsgleich mit den Befehlen im Code sein.
  - Besonderheit: Da P0.09/P0.10 genutzt werden, muss geprüft werden, ob die NFC-Schutzschaltung deaktiviert ist, da sonst die Signalflanken bei SPI-Geschwindigkeit zu stark verlangsamt werden.

Test 5: Analog-Digital-Wandler (ADC)

- Was testen? Korrekte Skalierung des Akku-Messwerts.
- Wie? Definierte Spannung (z.B. 3.7 V) an den Akku-Eingang anlegen. Spannung an TP_AKKU messen.
- Erwartung: Der gemessene ADC-Wert im Code muss mit der real anliegenden Spannung am Testpunkt übereinstimmen.

# 4. Herstellungstest (Produktion)

Ein automatisierter Prozess nutzt ein Nadelbett ("Testfixture"), um das Board in ca. 85-90 Sekunden zu prüfen.

Schritt | Messung | Testpunkt | Kriterium | Zeit
1 | Power-On | TP_VCC/GND | 3.3 V ±5% | 10 s
2 | I²C-Scan | TP_SDA/SCL | ACK von Sensor-ID | 15 s
3 | SPI-Check | SPI-Block | Register 0x0F / ID-Match | 15 s
4 | Flash-Test | SWD-Block | Firmware Verified | 20 s
5 | ADC-Check | TP_AKKU | Ruhend ±0.05 g / Spannung plausibel | 20 s
6 | Sticker | - | PASS / FAIL | 10 s

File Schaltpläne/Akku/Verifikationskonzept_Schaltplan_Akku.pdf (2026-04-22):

Verifikationskonzept Schaltplan Akku

Wir haben in unseren Schaltplan spezifische Testpunkte integriert, um die kritischen Spannungsversorgungen und die Akku-Überwachung des Moduls systematisch zu prüfen. Dadurch können Messungen direkt durchgeführt werden, ohne die eigentliche Elektronik oder bereits angeschlossene Komponenten zu beschädigen.

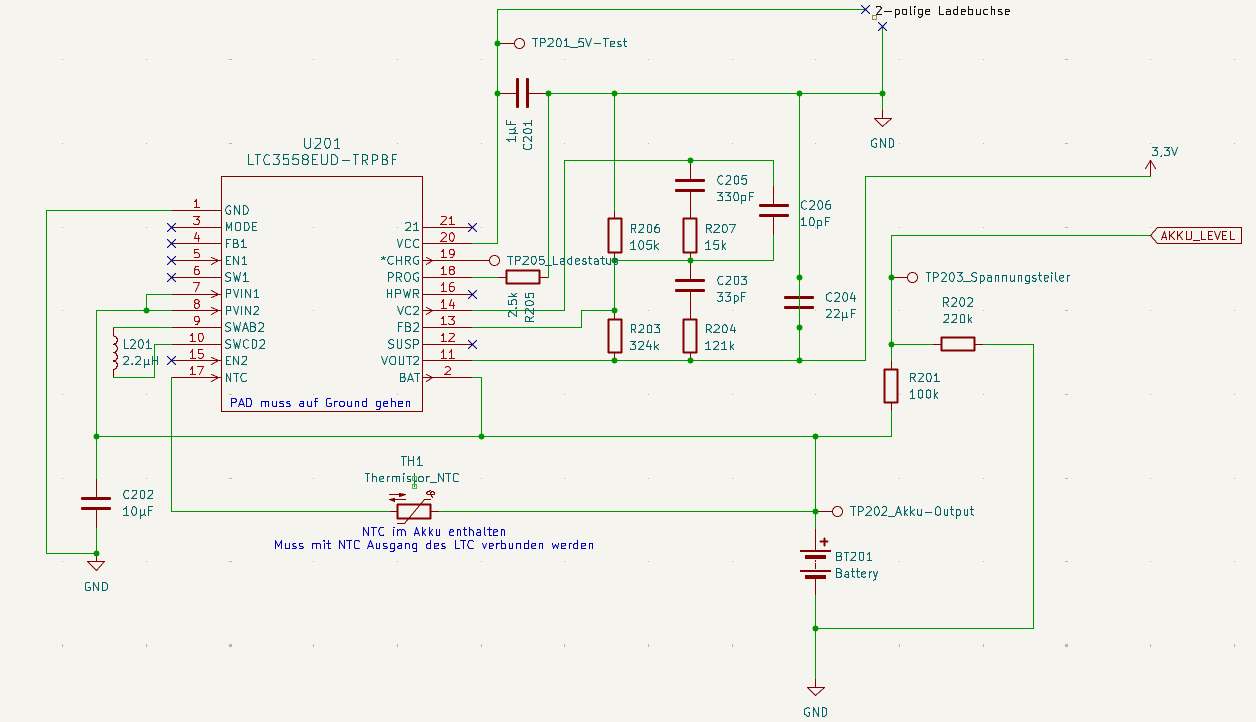
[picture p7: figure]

Testpunkte und ihr Zweck:

1. TP201 (5V Test) / GND: Sicherstellen, dass die 5V Versorgungsspannung von der Ladebuchse korrekt ankommt.
2. TP202 (Akku Output) / GND: Messung der Ausgangsspannung am Akku-Anschluss (Sollwert: zwischen 3V und 3,9V).
3. TP203 (Spannungsteiler) / GND: Kontrolle der reduzierten Spannung mit angelegten 3,7V für die AKKU_LEVEL Messung am Mikrocontroller.
4. TPVCC (3,3V Test) / GND: Messpunkt zur Überprüfung der stabilen 3,3-V-Versorgung direkt am Microcontroller.
5. TP205 (Charge Status) / GND: Überprüfung des Ladestatus-Signals vom LTC3558, um sicherzustellen, dass der Ladevorgang bei angeschlossener Versorgungsspannung aktiv ist.
1. Verifikationstests (Entwicklung)

Test 1: 5V Eingang prüfen

- Was testen? Kommen 5V über die Ladebuchse an?

- Wie? Multimeter (rote Sonde an TP1, schwarze an GND). Ladebuchse mit 5V Spannungsquelle verbinden.
- Erwartung: 4.9V – 5.1V. → TP1 bestätigt die korrekte Anbindung der Ladebuchse.

Test 2: Akku Output kontrollieren

- Was testen? Liefert der Akku-Pfad die gewünschte Spannung?
- Wie? Akku oder Netzteil am Akku-Anschluss anschließen. Messung mit Multimeter an TP2 gegen GND.
- Erwartung: Messung zwischen 3V und 3,9V → TP2 kontrolliert den stabilen Akku-Ausgang.

Test 3: Spannungsteiler (Akku-Überwachung)

- Was testen? Funktioniert der Spannungsteiler für die Messung der Akkuspannung?
- Wie? Bekannte Spannung an TP2 anlegen. Messung der Ausgangsspannung an TP3 gegen GND.
- Beispiel: Bei 3,0 V an TP2 wird eine Spannung von ca. 0,94 V an TP3 erwartet, bei 3,7 V ca. 1,16 V und bei 4,2 V ca. 1,31 V. Dies entspricht einem Ladezustand von ca. 0 % bis 100 %.
- Uout = Uin =

R2
R1+R2

=> ca. 31%

- Erwartung: Spannung proportional zum Teilerverhältnis (R1/R2). → TP3 zeigt das korrekte Signal für AKKU_LEVEL. Spannung an TP3 ist kleiner als TP2

Test 4: Systemspannung 3,3V

- Was testen? Ist die geregelte Systemspannung stabil vorhanden?
- Wie? Eingangsspannung anlegen, z. B. Batterie anschließen oder Labornetzteil einschalten. Anschließend Spannung am 3,3V-Pin des Microcontrollers (TPVCC) gegen GND mit dem Multimeter messen (optional Oszilloskop zur Ripple-Prüfung).
- Erwartung: 3,3 V ±5%.

TPVCC (aus Controller-Schaltplan) bestätigt eine korrekte und stabile System-Versorgung des Microcontrollers

Test 5: Ladefunktion (Charge Status)

- Was testen? Erkennt der LTC3558 die Ladespannung und aktiviert er den Ladevorgang?

- Wie? Anlegen von 5 V an die Ladebuchse, Anschluss eines Akkus oder einer geeigneten Ersatzlast an TP2 sowie Messung der Spannung an TP5 gegen GND.
- Erwartung:
- Ladevorgang aktiv: Spannung an TP5 liegt nahe 0V.
- Kein Ladevorgang/Voll: Spannung an TP5 entspricht der Pull-up-Spannung (meist 3,3V).

→ TP5 bestätigt die Logik der Ladeelektronik.

2. Herstellungstests (Produktion)

Automatisierter Inline-Test: Die Tests werden über eine Testfixture mit Federkontakten an den Testpunkten durchgeführt.

Schritt | Messung | Testpunkt | Kriterium | Zeit
1 | 5V Eingang | TP201/GND | 5,0 V ± 2% | 10s
2 | Akku Output | TP202/GND | 3,0V ± 5% | 10s
3 | Pegel-Check | TP203/GND | TP3 sollte ± 5% 31% von TP2 sein | 15s
4 | System 3,3V | TPVCC (MCU) / GND | 3,3V ± 5% | 10s
5 | Ladefunktion | TP205/GND | < 0,5 V (bei 5V an TP1) | 10s
6 | Endergebnis | | PASS oder FAIL | 5s

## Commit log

2026-03-06 Create Git Hub Projekt Erklärung
    File zu Erklärung des Git Hub Projekts im Repository und dessen Benutzung
2026-03-06 System Architektur eingefügt
    Added flowchart diagram for system architecture and updated requirements.
2026-03-07 PCB design guidelines
2026-03-08 Austauschen der Systemarchitekur
2026-03-31 Expand functionality and glossary sections in documentation
    Added detailed functionality description and glossary for the wearable device.
2026-04-12 Add Akku files
    [Akku.kicad_pcb, Akku.kicad_sch]
2026-04-12 Akku Schaltplan
    [Akku.kicad_pcb, Akku.kicad_sch]
2026-04-12 added files for microcontroller
    [bom_wearables.xlsx, microcontroller.kicad_sch]
2026-04-14 Aktualisierung Schaltplan
    [Akku.kicad_sch]
2026-04-14 added revised schematic in zip folder and new verification document for microcontroller
    [microcontroller.kicad_sch]
2026-04-15 Add files via upload
    stand 15.04.
    Fehlend Eventuell Verbindung Interrupt vom MAX
    Fehlend Verzögerrung von 5V auf LED zu VDD am MAX - nicht so schlimm wenn VDD nicht alzu spät kommt
    Softwareseitige lösung? Sonst FET+RC-Verzögerrung von 5V
2026-04-15 added revised bom
    [bom_wearables.xlsx]
2026-04-16 changed ground direction to down
    [Schaltplan_Datenverarbeitung.kicad_sch]
